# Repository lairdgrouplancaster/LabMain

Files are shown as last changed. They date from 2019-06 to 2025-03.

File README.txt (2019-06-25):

How to use this repository:
(Note: All commands are to be entered without quotation marks)

First off, you will need to install Git onto your local machine. Follow this link: "https://git-scm.com/" and download the appropriate version. If unsure whether git is installed on your local machine, open a command prompt and type: "git --version" and see whether it is installed. 

To start with, open up either the command prompt or GitBash and configure your Git username and email, which will be used to identify you as the author for each commit. This is done by entering the following: "git config --global user.name "YOUR_USERNAME"" and "git config --global user.email "YOUR_EMAIL@example.com""

Once this has been done, you can clone the repository to your local device by inputting the following command: "git clone https://github.com/lairdgrouplancaster/LabMain.git" which will then copy all of the files from the repository and place them in a folder of the same name. 

Once cloned, you can navigate to the directory in the command prompt, and then check to see your remote repositories by using: "git remote -v" This will usually show what remote repository it is (usually origin). If this isn't showing, you can manually add these repositories. 

AT THE START OF EACH SESSION: Ensure that you have an up-to-date copy of the repository by using: "git pull origin master"

To check the changes made in the local directory, you can use "git status" to check any modifications that you have made to the file itself, and use "git diff" to view the differences between the local changes to the repository versions that were previously cloned/pulled

You can add changes to the local version of the repository by using the following command: "git add FILE OR FOLDER" or "git add ." to ready either a file, folder or all files and folders for commiting. Then input: "git commit -m "COMMENT ON CHANGE AND INTENTION"" 

To push all of the local commits to the remote repository on GitHub, you can use the following command: "git push origin master", where you can replace origin for the name of a different remote repository and master for a different branch. 

All of this can also be done in the browser as well, and any additional pieces of information (Creating branches, forks etc.) can be found online, usually on the GitHub website itself.

Using a previous version of the repository:

After cloning the repository, look at the recent logs by using the command: "git log --oneline". Select the version of the roll back you want, and then make note of the first 5 characters of the unique number and use: "git checkout (5 characters)". Alternatively, you can use this function based on dates instead, for example if I wanted to revert back 10 days ago, I would input: "git checkout @{10.days.ago}"

Current Files: 

.gitignore: This file tells Git what files and folders to ignore when pulling or pushing updates. Currently only ignores the cache folder for Python.
LICENSE: This is where all licenses for software can be found, and can be added. Currently contains license for GNU
README: Current file, explains how to get started and what files are contained in this repository

Current Folders:

LiamColman: Liam's work uploaded onto Github for storage

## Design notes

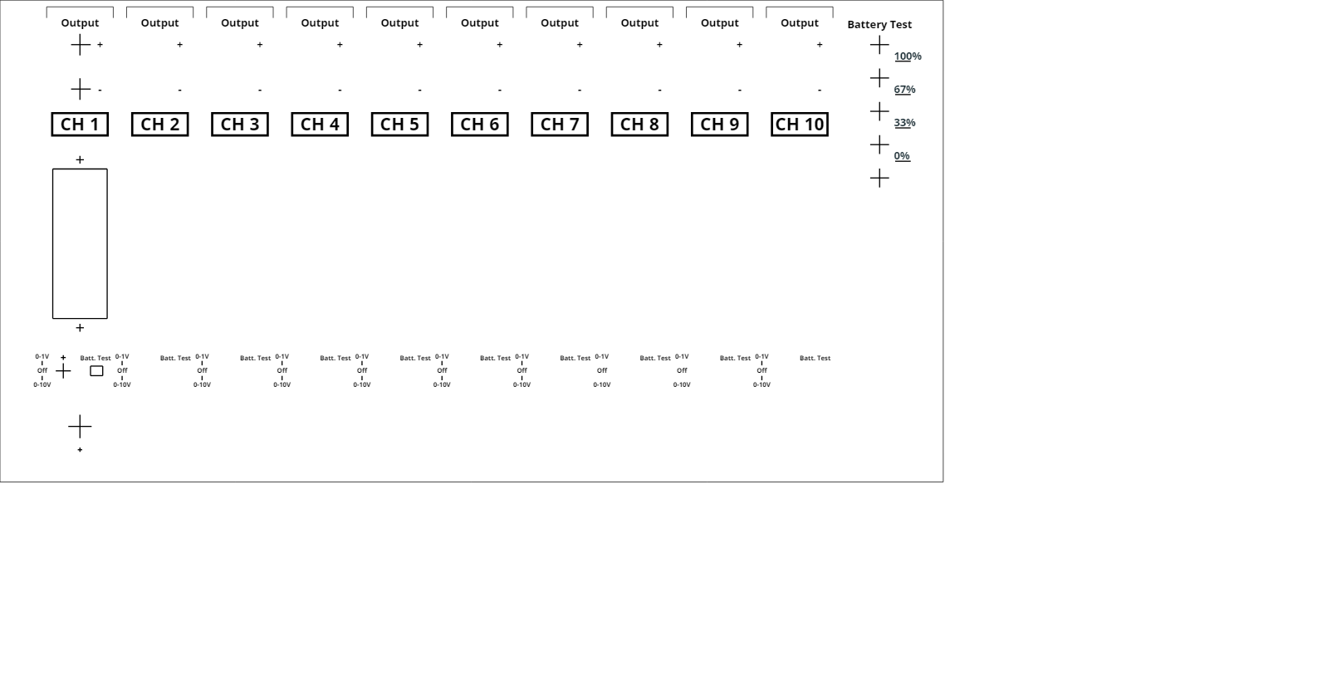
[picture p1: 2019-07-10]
LiamsWork/VoltageRegulator/FrontPanelDesign/VoltageSourceFrontPanel.png

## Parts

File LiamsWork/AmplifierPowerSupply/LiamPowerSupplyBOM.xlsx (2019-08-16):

Bill of materials for amplifier power supply
Part Name | Manufacturer | Manufacturer Part Number | PCB Reference | Qty | Description | SMD, TH or Other (BGA, QFN etc.) | Comment
1206 Capacitor | PCBTrain Free Stock | 1206-1uF-50V (MC1206B104K500CT) | C1, C3 | 2 | CAPACITOR; 1206; 50V; 10%; X7R; -55+125C | SMD | Farnell (https://uk.farnell.com/multicomp/mc1206b104k500ct/cap-mlcc-x7r-100nf-50v-1206/dp/1759361)
1206 Capacitor | AVX Corporation | TPSA106K010R0900 | C2, C4 | 2 | Tantalum capacitor; 1206; 10V; 10u | SMD |  | Digikey (https://www.digikey.co.uk/product-detail/en/avx-corporation/TPSA106K010R0900/478-1751-1-ND/564783)
Fuseholder | EATON BUSSMANN SERIES | HTC-100M | F1, F2 | 2 | Fuseholder; 5A; 250V | TH | Farnell (https://uk.farnell.com/eaton-bussmann-series/htc-100m/fuse-holder-pcb-250v-5a/dp/2550634)
2 pin headers | SULLINS CONNECTOR SOLUTIONS | GEC01DAAN | J1, J2, J3, J4 | 4 | Male header; 2 pin; 2 row; 2.54mm pitch | TH |  | Digikey (https://www.digikey.co.uk/product-detail/en/sullins-connector-solutions/GEC01DAAN/S9682-ND/4552155)
4 pin header | SULLINS CONNECTOR SOLUTIONS | PEC04SAAN | J5 | 1 | Male header; 4 pin; 1 row; 2.54mm pitch | TH |  | Digikey (https://www.digikey.com/product-detail/en/sullins-connector-solutions/PEC04SAAN/S1012E-04-ND/859157)
Low-Dropout voltage regulator | TEXAS INSTRUMENTS | TPS7250 | LD01 | 1 | 5V output; low quiescent current; power good status; PDIP package | TH | Mouser (https://www.mouser.co.uk/ProductDetail/Texas-Instruments/TPS7250QP?qs=sGAEpiMZZMsGz1a6aV8DcPXeWoVS0FnzUEk95Vl5yAE%3D) | Texas Instuments (http://www.ti.com/product/TPS72)
DIP Socket | Winslow | W30508TRC | LD01 | 1 | 8 pin; 7.62mm row spacing; 2.54mm pitch | TH |  | RS Components (https://uk.rs-online.com/web/p/dil-sockets/0813115/)
Quad transistors | CENTRAL SEMICONDUCTOR | MPQ3904 | Q1 | 1 | Quad bipolar transistors; NPN; TO-116 package | TH | Mouser (https://www.mouser.co.uk/ProductDetail/Central-Semiconductor/MPQ3904?qs=Ypxpq5eNvNUHCP5TyaTdcA%3D%3D)
DIP Socket | ARIES | 14-3518-10 | Q1 | 1 | 14 pin; 7.62mm row spacing; 2.54mm pitch | TH | Farnell (https://uk.farnell.com/aries/14-3518-10/socket-dip-14way/dp/1674785)
0805 Resistor | PCBTrain Free Stock | 0805-1K2 | R1, R6 | 2 | RESISTOR; 0805; 0.125W; 100ppm; 1%; 150V; -55+125C; 1.2k | SMD
0805 Resistor | PCBTrain Free Stock | 0805-240K | R2 | 1 | RESISTOR; 0805; 0.125W; 100ppm; 1%; 150V; -55+125C; 240k | SMD
0805 Resistor | PCBTrain Free Stock | 0805-150R | R3, R5 | 2 | RESISTOR; 0805; 0.125W; 100ppm; 1%; 150V; -55+125C; 150R | SMD
0805 Resistor | PCBTrain Free Stock | 0805-270R | R4 | 1 | RESISTOR; 0805; 0.125W; 100ppm; 1%; 150V; -55+125C; 270R | SMD
0805 Resistor | PCBTrain Free Stock | 0805-56R | R7 | 1 | RESISTOR; 0805; 0.125W; 100ppm; 1%; 150V; -55+125C; 56R | SMD
0805 Resistor | PCBTrain Free Stock | 0805-33R | R8 | 1 | RESISTOR; 0805; 0.125W; 100ppm; 1%; 150V; -55+125C: 33R | SMD
0805 Resistor | PCBTrain Free Stock | 0805-10R | R9 | 1 | RESISTOR; 0805; 0.125W; 100ppm; 1%; 150V; -55+125C; 10R | SMD
0805 Resistor | PCBTrain Free Stock | 0805-470K | R10 | 1 | RESISTOR; 0805; 0.125W; 100ppm; 1%; 150V; -55+125C; 470k | SMD
0805 Resistor | PCBTrain Free Stock | 0805-100R | R11, R12 | 2 | RESISTOR; 0805; 0.125W; 100ppm; 1%; 150V; -55+125C; 100R | SMD
Thryristor | STMicroelectronics | X0205MA 1BA2 | SCR1 | 1 | 1.25A sensitive gate SCR | TH | Mouser (https://www.mouser.co.uk/ProductDetail/STMicroelectronics/X0205MA-1BA2/?qs=rbJCU8ygG7CkfsITI88o%2Fw%3D%3D)
Zener diode | Panasonic | DZ2W04300L | Z1 | 1 | 4.3V zener diode; Mini2 package | SMD | Mouser (https://www.mouser.co.uk/ProductDetail/Panasonic/DZ2W04300L?qs=VO99igtUVKlrlP3g8MwZQg%3D%3D) | Digikey (https://www.digikey.com/product-detail/en/panasonic-electronic-components/DZ2W04300L/DZ2W04300LCT-ND/3595040)

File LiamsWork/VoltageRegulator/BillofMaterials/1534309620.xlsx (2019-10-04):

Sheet: 0201 RESISTORS
VALUE | NEL P/N | DESCRIPTION (type; size; power; TC; tolerance; volt.; temp.;)
0R0 | 0201-0R | RESISTOR; 0201; 0.05W; 400ppm; ≤50mΩ; 25V; -55+125C
1R0 | 0201-1R | RESISTOR; 0201; 0.05W; 400ppm; 1%; 25V; -55+125C;
1R1 | 0201-1R1 | RESISTOR; 0201; 0.05W; 400ppm; 1%; 25V; -55+125C;
1R2 | 0201-1R2 | RESISTOR; 0201; 0.05W; 400ppm; 1%; 25V; -55+125C;
1R5 | 0201-1R5 | RESISTOR; 0201; 0.05W; 400ppm; 1%; 25V; -55+125C;
1R8 | 0201-1R8 | RESISTOR; 0201; 0.05W; 400ppm; 1%; 25V; -55+125C;
2R0 | 0201-2R | RESISTOR; 0201; 0.05W; 400ppm; 1%; 25V; -55+125C;
2R2 | 0201-2R2 | RESISTOR; 0201; 0.05W; 400ppm; 1%; 25V; -55+125C;
2R7 | 0201-2R7 | RESISTOR; 0201; 0.05W; 400ppm; 1%; 25V; -55+125C;
3R0 | 0201-3R | RESISTOR; 0201; 0.05W; 400ppm; 1%; 25V; -55+125C;
3R3 | 0201-3R3 | RESISTOR; 0201; 0.05W; 400ppm; 1%; 25V; -55+125C;
3R9 | 0201-3R9 | RESISTOR; 0201; 0.05W; 400ppm; 1%; 25V; -55+125C;
4R7 | 0201-4R7 | RESISTOR; 0201; 0.05W; 400ppm; 1%; 25V; -55+125C;
5R1 | 0201-5R1 | RESISTOR; 0201; 0.05W; 400ppm; 1%; 25V; -55+125C;
5R6 | 0201-5R6 | RESISTOR; 0201; 0.05W; 400ppm; 1%; 25V; -55+125C;
6R8 | 0201-6R8 | RESISTOR; 0201; 0.05W; 400ppm; 1%; 25V; -55+125C;
8R2 | 0201-8R2 | RESISTOR; 0201; 0.05W; 400ppm; 1%; 25V; -55+125C;
10R | 0201-10R | RESISTOR; 0201; 0.05W; 200ppm; 1%; 25V; -55+125C;
11R | 0201-11R | RESISTOR; 0201; 0.05W; 200ppm; 1%; 25V; -55+125C;
12R | 0201-12R | RESISTOR; 0201; 0.05W; 200ppm; 1%; 25V; -55+125C;
13R | 0201-13R | RESISTOR; 0201; 0.05W; 200ppm; 1%; 25V; -55+125C;
15R | 0201-15R | RESISTOR; 0201; 0.05W; 200ppm; 1%; 25V; -55+125C;
16R | 0201-16R | RESISTOR; 0201; 0.05W; 200ppm; 1%; 25V; -55+125C;
18R | 0201-18R | RESISTOR; 0201; 0.05W; 200ppm; 1%; 25V; -55+125C;
20R | 0201-20R | RESISTOR; 0201; 0.05W; 200ppm; 1%; 25V; -55+125C;
22R | 0201-22R | RESISTOR; 0201; 0.05W; 200ppm; 1%; 25V; -55+125C;
24R | 0201-24R | RESISTOR; 0201; 0.05W; 200ppm; 1%; 25V; -55+125C;
27R | 0201-27R | RESISTOR; 0201; 0.05W; 200ppm; 1%; 25V; -55+125C;
30R | 0201-30R | RESISTOR; 0201; 0.05W; 200ppm; 1%; 25V; -55+125C;
33R | 0201-33R | RESISTOR; 0201; 0.05W; 200ppm; 1%; 25V; -55+125C;
36R | 0201-36R | RESISTOR; 0201; 0.05W; 200ppm; 1%; 25V; -55+125C;
39R | 0201-39R | RESISTOR; 0201; 0.05W; 200ppm; 1%; 25V; -55+125C;
43R | 0201-43R | RESISTOR; 0201; 0.05W; 200ppm; 1%; 25V; -55+125C;
47R | 0201-47R | RESISTOR; 0201; 0.05W; 200ppm; 1%; 25V; -55+125C;
51R | 0201-51R | RESISTOR; 0201; 0.05W; 200ppm; 1%; 25V; -55+125C;
56R | 0201-56R | RESISTOR; 0201; 0.05W; 200ppm; 1%; 25V; -55+125C;
62R | 0201-62R | RESISTOR; 0201; 0.05W; 200ppm; 1%; 25V; -55+125C;
68R | 0201-68R | RESISTOR; 0201; 0.05W; 200ppm; 1%; 25V; -55+125C;
75R | 0201-75R | RESISTOR; 0201; 0.05W; 200ppm; 1%; 25V; -55+125C;
82R | 0201-82R | RESISTOR; 0201; 0.05W; 200ppm; 1%; 25V; -55+125C;
91R | 0201-91R | RESISTOR; 0201; 0.05W; 200ppm; 1%; 25V; -55+125C;
100R | 0201-100R | RESISTOR; 0201; 0.05W; 200ppm; 1%; 25V; -55+125C;
110R | 0201-110R | RESISTOR; 0201; 0.05W; 200ppm; 1%; 25V; -55+125C;
120R | 0201-120R | RESISTOR; 0201; 0.05W; 200ppm; 1%; 25V; -55+125C;
130R | 0201-130R | RESISTOR; 0201; 0.05W; 200ppm; 1%; 25V; -55+125C;
150R | 0201-150R | RESISTOR; 0201; 0.05W; 200ppm; 1%; 25V; -55+125C;
160R | 0201-160R | RESISTOR; 0201; 0.05W; 200ppm; 1%; 25V; -55+125C;
180R | 0201-180R | RESISTOR; 0201; 0.05W; 200ppm; 1%; 25V; -55+125C;
200R | 0201-200R | RESISTOR; 0201; 0.05W; 200ppm; 1%; 25V; -55+125C;
220R | 0201-220R | RESISTOR; 0201; 0.05W; 200ppm; 1%; 25V; -55+125C;
240R | 0201-240R | RESISTOR; 0201; 0.05W; 200ppm; 1%; 25V; -55+125C;
270R | 0201-270R | RESISTOR; 0201; 0.05W; 200ppm; 1%; 25V; -55+125C;
300R | 0201-300R | RESISTOR; 0201; 0.05W; 200ppm; 1%; 25V; -55+125C;
330R | 0201-330R | RESISTOR; 0201; 0.05W; 200ppm; 1%; 25V; -55+125C;
360R | 0201-360R | RESISTOR; 0201; 0.05W; 200ppm; 1%; 25V; -55+125C;
390R | 0201-390R | RESISTOR; 0201; 0.05W; 200ppm; 1%; 25V; -55+125C;
430R | 0201-430R | RESISTOR; 0201; 0.05W; 200ppm; 1%; 25V; -55+125C;
470R | 0201-470R | RESISTOR; 0201; 0.05W; 200ppm; 1%; 25V; -55+125C;
510R | 0201-510R | RESISTOR; 0201; 0.05W; 200ppm; 1%; 25V; -55+125C;
560R | 0201-560R | RESISTOR; 0201; 0.05W; 200ppm; 1%; 25V; -55+125C;
620R | 0201-620R | RESISTOR; 0201; 0.05W; 200ppm; 1%; 25V; -55+125C;
680R | 0201-680R | RESISTOR; 0201; 0.05W; 200ppm; 1%; 25V; -55+125C;
750R | 0201-750R | RESISTOR; 0201; 0.05W; 200ppm; 1%; 25V; -55+125C;
820R | 0201-820R | RESISTOR; 0201; 0.05W; 200ppm; 1%; 25V; -55+125C;
910R | 0201-910R | RESISTOR; 0201; 0.05W; 200ppm; 1%; 25V; -55+125C;
1K0 | 0201-1K | RESISTOR; 0201; 0.05W; 200ppm; 1%; 25V; -55+125C;
1K1 | 0201-1K1 | RESISTOR; 0201; 0.05W; 200ppm; 1%; 25V; -55+125C;
1K2 | 0201-1K2 | RESISTOR; 0201; 0.05W; 200ppm; 1%; 25V; -55+125C;
1K3 | 0201-1K3 | RESISTOR; 0201; 0.05W; 200ppm; 1%; 25V; -55+125C;
1K5 | 0201-1K5 | RESISTOR; 0201; 0.05W; 200ppm; 1%; 25V; -55+125C;
1K6 | 0201-1K6 | RESISTOR; 0201; 0.05W; 200ppm; 1%; 25V; -55+125C;
1K8 | 0201-1K8 | RESISTOR; 0201; 0.05W; 200ppm; 1%; 25V; -55+125C;
2K0 | 0201-2K | RESISTOR; 0201; 0.05W; 200ppm; 1%; 25V; -55+125C;
2K2 | 0201-2K2 | RESISTOR; 0201; 0.05W; 200ppm; 1%; 25V; -55+125C;
2K4 | 0201-2K4 | RESISTOR; 0201; 0.05W; 200ppm; 1%; 25V; -55+125C;
2K7 | 0201-2K7 | RESISTOR; 0201; 0.05W; 200ppm; 1%; 25V; -55+125C;
3K0 | 0201-3K | RESISTOR; 0201; 0.05W; 200ppm; 1%; 25V; -55+125C;
3K3 | 0201-3K3 | RESISTOR; 0201; 0.05W; 200ppm; 1%; 25V; -55+125C;
3K6 | 0201-3K6 | RESISTOR; 0201; 0.05W; 200ppm; 1%; 25V; -55+125C;
3K9 | 0201-3K9 | RESISTOR; 0201; 0.05W; 200ppm; 1%; 25V; -55+125C;
4K3 | 0201-4K3 | RESISTOR; 0201; 0.05W; 200ppm; 1%; 25V; -55+125C;
4K7 | 0201-4K7 | RESISTOR; 0201; 0.05W; 200ppm; 1%; 25V; -55+125C;
5K1 | 0201-5K1 | RESISTOR; 0201; 0.05W; 200ppm; 1%; 25V; -55+125C;
5K6 | 0201-5K6 | RESISTOR; 0201; 0.05W; 200ppm; 1%; 25V; -55+125C;
6K2 | 0201-6K2 | RESISTOR; 0201; 0.05W; 200ppm; 1%; 25V; -55+125C;
6K8 | 0201-6K8 | RESISTOR; 0201; 0.05W; 200ppm; 1%; 25V; -55+125C;
7K5 | 0201-7K5 | RESISTOR; 0201; 0.05W; 200ppm; 1%; 25V; -55+125C;
8K2 | 0201-8K2 | RESISTOR; 0201; 0.05W; 200ppm; 1%; 25V; -55+125C;
9K1 | 0201-9K1 | RESISTOR; 0201; 0.05W; 200ppm; 1%; 25V; -55+125C;
10K | 0201-10K | RESISTOR; 0201; 0.05W; 200ppm; 1%; 25V; -55+125C;
11K | 0201-11K | RESISTOR; 0201; 0.05W; 200ppm; 1%; 25V; -55+125C;
12K | 0201-12K | RESISTOR; 0201; 0.05W; 200ppm; 1%; 25V; -55+125C;
13K | 0201-13K | RESISTOR; 0201; 0.05W; 200ppm; 1%; 25V; -55+125C;
15K | 0201-15K | RESISTOR; 0201; 0.05W; 200ppm; 1%; 25V; -55+125C;
16K | 0201-16K | RESISTOR; 0201; 0.05W; 200ppm; 1%; 25V; -55+125C;
18K | 0201-18K | RESISTOR; 0201; 0.05W; 200ppm; 1%; 25V; -55+125C;
20K | 0201-20K | RESISTOR; 0201; 0.05W; 200ppm; 1%; 25V; -55+125C;
22K | 0201-22K | RESISTOR; 0201; 0.05W; 200ppm; 1%; 25V; -55+125C;
24K | 0201-24K | RESISTOR; 0201; 0.05W; 200ppm; 1%; 25V; -55+125C;
27K | 0201-27K | RESISTOR; 0201; 0.05W; 200ppm; 1%; 25V; -55+125C;
30K | 0201-30K | RESISTOR; 0201; 0.05W; 200ppm; 1%; 25V; -55+125C;
33K | 0201-33K | RESISTOR; 0201; 0.05W; 200ppm; 1%; 25V; -55+125C;
36K | 0201-36K | RESISTOR; 0201; 0.05W; 200ppm; 1%; 25V; -55+125C;
39K | 0201-39K | RESISTOR; 0201; 0.05W; 200ppm; 1%; 25V; -55+125C;
43K | 0201-43K | RESISTOR; 0201; 0.05W; 200ppm; 1%; 25V; -55+125C;
47K | 0201-47K | RESISTOR; 0201; 0.05W; 200ppm; 1%; 25V; -55+125C;
51K | 0201-51K | RESISTOR; 0201; 0.05W; 200ppm; 1%; 25V; -55+125C;
56K | 0201-56K | RESISTOR; 0201; 0.05W; 200ppm; 1%; 25V; -55+125C;
62K | 0201-62K | RESISTOR; 0201; 0.05W; 200ppm; 1%; 25V; -55+125C;
68K | 0201-68K | RESISTOR; 0201; 0.05W; 200ppm; 1%; 25V; -55+125C;
75K | 0201-75K | RESISTOR; 0201; 0.05W; 200ppm; 1%; 25V; -55+125C;
82K | 0201-82K | RESISTOR; 0201; 0.05W; 200ppm; 1%; 25V; -55+125C;
91K | 0201-91K | RESISTOR; 0201; 0.05W; 200ppm; 1%; 25V; -55+125C;
100K | 0201-100K | RESISTOR; 0201; 0.05W; 200ppm; 1%; 25V; -55+125C;
110K | 0201-110K | RESISTOR; 0201; 0.05W; 200ppm; 1%; 25V; -55+125C;
120K | 0201-120K | RESISTOR; 0201; 0.05W; 200ppm; 1%; 25V; -55+125C;
150K | 0201-150K | RESISTOR; 0201; 0.05W; 200ppm; 1%; 25V; -55+125C;
160K | 0201-160K | RESISTOR; 0201; 0.05W; 200ppm; 1%; 25V; -55+125C;
180K | 0201-180K | RESISTOR; 0201; 0.05W; 200ppm; 1%; 25V; -55+125C;
200K | 0201-200K | RESISTOR; 0201; 0.05W; 200ppm; 1%; 25V; -55+125C;
220K | 0201-220K | RESISTOR; 0201; 0.05W; 200ppm; 1%; 25V; -55+125C;
240K | 0201-240K | RESISTOR; 0201; 0.05W; 200ppm; 1%; 25V; -55+125C;
270K | 0201-270K | RESISTOR; 0201; 0.05W; 200ppm; 1%; 25V; -55+125C;
300K | 0201-300K | RESISTOR; 0201; 0.05W; 200ppm; 1%; 25V; -55+125C;
330K | 0201-330K | RESISTOR; 0201; 0.05W; 200ppm; 1%; 25V; -55+125C;
360K | 0201-360K | RESISTOR; 0201; 0.05W; 200ppm; 1%; 25V; -55+125C;
390K | 0201-390K | RESISTOR; 0201; 0.05W; 200ppm; 1%; 25V; -55+125C;
430K | 0201-430K | RESISTOR; 0201; 0.05W; 200ppm; 1%; 25V; -55+125C;
470K | 0201-470K | RESISTOR; 0201; 0.05W; 200ppm; 1%; 25V; -55+125C;
510K | 0201-510K | RESISTOR; 0201; 0.05W; 200ppm; 1%; 25V; -55+125C;
560K | 0201-560K | RESISTOR; 0201; 0.05W; 200ppm; 1%; 25V; -55+125C;
620K | 0201-620K | RESISTOR; 0201; 0.05W; 200ppm; 1%; 25V; -55+125C;
680K | 0201-680K | RESISTOR; 0201; 0.05W; 200ppm; 1%; 25V; -55+125C;
750K | 0201-750K | RESISTOR; 0201; 0.05W; 200ppm; 1%; 25V; -55+125C;
820K | 0201-820K | RESISTOR; 0201; 0.05W; 200ppm; 1%; 25V; -55+125C;
910K | 0201-910K | RESISTOR; 0201; 0.05W; 200ppm; 1%; 25V; -55+125C;
1M0 | 0201-1M | RESISTOR; 0201; 0.05W; 200ppm; 1%; 25V; -55+125C;
1M2 | 0201-1M2 | RESISTOR; 0201; 0.05W; 200ppm; 1%; 25V; -55+125C;
1M3 | 0201-1M3 | RESISTOR; 0201; 0.05W; 200ppm; 1%; 25V; -55+125C;
1M5 | 0201-1M5 | RESISTOR; 0201; 0.05W; 200ppm; 1%; 25V; -55+125C;
1M6 | 0201-1M6 | RESISTOR; 0201; 0.05W; 200ppm; 1%; 25V; -55+125C;
1M8 | 0201-1M8 | RESISTOR; 0201; 0.05W; 200ppm; 1%; 25V; -55+125C;
2M0 | 0201-2M | RESISTOR; 0201; 0.05W; 200ppm; 1%; 25V; -55+125C;
2M2 | 0201-2M2 | RESISTOR; 0201; 0.05W; 200ppm; 1%; 25V; -55+125C;
2M7 | 0201-2M7 | RESISTOR; 0201; 0.05W; 200ppm; 1%; 25V; -55+125C;
3M0 | 0201-3M | RESISTOR; 0201; 0.05W; 200ppm; 1%; 25V; -55+125C;
3M3 | 0201-3M3 | RESISTOR; 0201; 0.05W; 200ppm; 1%; 25V; -55+125C;
3M6 | 0201-3M6 | RESISTOR; 0201; 0.05W; 200ppm; 1%; 25V; -55+125C;
3M9 | 0201-3M9 | RESISTOR; 0201; 0.05W; 200ppm; 1%; 25V; -55+125C;
4M7 | 0201-4M7 | RESISTOR; 0201; 0.05W; 200ppm; 1%; 25V; -55+125C;
5M1 | 0201-5M1 | RESISTOR; 0201; 0.05W; 200ppm; 1%; 25V; -55+125C;
6M8 | 0201-6M8 | RESISTOR; 0201; 0.05W; 200ppm; 1%; 25V; -55+125C;
8M2 | 0201-8M2 | RESISTOR; 0201; 0.05W; 200ppm; 1%; 25V; -55+125C;
10M | 0201-10M | RESISTOR; 0201; 0.05W; 200ppm; 1%; 25V; -55+125C;

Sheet: 0402 RESISTORS
VALUE | NEL P/N | DESCRIPTION (type; size; power; TC; tolerance; volt.; temp.;)
0R0 | 0402-0R | RESISTOR; 0402; 0.0625W; 400ppm; ≤50mΩ; 50V; -55+125C
1R0 | 0402-1R | RESISTOR; 0402; 0.0625W; 400ppm; 1%; 50V; -55+125C
1R1 | 0402-1R1 | RESISTOR; 0402; 0.0625W; 400ppm; 1%; 50V; -55+125C
1R2 | 0402-1R2 | RESISTOR; 0402; 0.0625W; 400ppm; 1%; 50V; -55+125C
1R3 | 0402-1R3 | RESISTOR; 0402; 0.0625W; 400ppm; 1%; 50V; -55+125C
1R5 | 0402-1R5 | RESISTOR; 0402; 0.0625W; 400ppm; 1%; 50V; -55+125C
1R6 | 0402-1R6 | RESISTOR; 0402; 0.0625W; 400ppm; 1%; 50V; -55+125C
1R8 | 0402-1R8 | RESISTOR; 0402; 0.0625W; 400ppm; 1%; 50V; -55+125C
2R0 | 0402-2R | RESISTOR; 0402; 0.0625W; 400ppm; 1%; 50V; -55+125C
2R2 | 0402-2R2 | RESISTOR; 0402; 0.0625W; 400ppm; 1%; 50V; -55+125C
2R4 | 0402-2R4 | RESISTOR; 0402; 0.0625W; 400ppm; 1%; 50V; -55+125C
2R7 | 0402-2R7 | RESISTOR; 0402; 0.0625W; 400ppm; 1%; 50V; -55+125C
3R0 | 0402-3R | RESISTOR; 0402; 0.0625W; 400ppm; 1%; 50V; -55+125C
3R3 | 0402-3R3 | RESISTOR; 0402; 0.0625W; 400ppm; 1%; 50V; -55+125C
3R6 | 0402-3R6 | RESISTOR; 0402; 0.0625W; 400ppm; 1%; 50V; -55+125C
3R9 | 0402-3R9 | RESISTOR; 0402; 0.0625W; 400ppm; 1%; 50V; -55+125C
4R3 | 0402-4R3 | RESISTOR; 0402; 0.0625W; 400ppm; 1%; 50V; -55+125C
4R7 | 0402-4R7 | RESISTOR; 0402; 0.0625W; 400ppm; 1%; 50V; -55+125C
5R1 | 0402-5R1 | RESISTOR; 0402; 0.0625W; 400ppm; 1%; 50V; -55+125C
5R6 | 0402-5R6 | RESISTOR; 0402; 0.0625W; 400ppm; 1%; 50V; -55+125C
6R2 | 0402-6R2 | RESISTOR; 0402; 0.0625W; 400ppm; 1%; 50V; -55+125C
6R8 | 0402-6R8 | RESISTOR; 0402; 0.0625W; 400ppm; 1%; 50V; -55+125C
7R5 | 0402-7R5 | RESISTOR; 0402; 0.0625W; 400ppm; 1%; 50V; -55+125C
8R2 | 0402-8R2 | RESISTOR; 0402; 0.0625W; 400ppm; 1%; 50V; -55+125C
9R1 | 0402-9R1 | RESISTOR; 0402; 0.0625W; 400ppm; 1%; 50V; -55+125C
10R | 0402-10R | RESISTOR; 0402; 0.0625W; 200ppm; 1%; 50V; -55+125C
11R | 0402-11R | RESISTOR; 0402; 0.0625W; 200ppm; 1%; 50V; -55+125C
12R | 0402-12R | RESISTOR; 0402; 0.0625W; 200ppm; 1%; 50V; -55+125C
13R | 0402-13R | RESISTOR; 0402; 0.0625W; 200ppm; 1%; 50V; -55+125C
15R | 0402-15R | RESISTOR; 0402; 0.0625W; 200ppm; 1%; 50V; -55+125C
16R | 0402-16R | RESISTOR; 0402; 0.0625W; 200ppm; 1%; 50V; -55+125C
18R | 0402-18R | RESISTOR; 0402; 0.0625W; 200ppm; 1%; 50V; -55+125C
20R | 0402-20R | RESISTOR; 0402; 0.0625W; 200ppm; 1%; 50V; -55+125C
22R | 0402-22R | RESISTOR; 0402; 0.0625W; 200ppm; 1%; 50V; -55+125C
24R | 0402-24R | RESISTOR; 0402; 0.0625W; 200ppm; 1%; 50V; -55+125C
27R | 0402-27R | RESISTOR; 0402; 0.0625W; 200ppm; 1%; 50V; -55+125C
30R | 0402-30R | RESISTOR; 0402; 0.0625W; 200ppm; 1%; 50V; -55+125C
33R | 0402-33R | RESISTOR; 0402; 0.0625W; 200ppm; 1%; 50V; -55+125C
36R | 0402-36R | RESISTOR; 0402; 0.0625W; 200ppm; 1%; 50V; -55+125C
39R | 0402-39R | RESISTOR; 0402; 0.0625W; 200ppm; 1%; 50V; -55+125C
43R | 0402-43R | RESISTOR; 0402; 0.0625W; 200ppm; 1%; 50V; -55+125C
47R | 0402-47R | RESISTOR; 0402; 0.0625W; 200ppm; 1%; 50V; -55+125C
51R | 0402-51R | RESISTOR; 0402; 0.0625W; 200ppm; 1%; 50V; -55+125C
56R | 0402-56R | RESISTOR; 0402; 0.0625W; 200ppm; 1%; 50V; -55+125C
62R | 0402-62R | RESISTOR; 0402; 0.0625W; 200ppm; 1%; 50V; -55+125C
68R | 0402-68R | RESISTOR; 0402; 0.0625W; 200ppm; 1%; 50V; -55+125C
75R | 0402-75R | RESISTOR; 0402; 0.0625W; 200ppm; 1%; 50V; -55+125C
82R | 0402-82R | RESISTOR; 0402; 0.0625W; 200ppm; 1%; 50V; -55+125C
91R | 0402-91R | RESISTOR; 0402; 0.0625W; 200ppm; 1%; 50V; -55+125C
100R | 0402-100R | RESISTOR; 0402; 0.0625W; 100ppm; 1%; 50V; -55+125C
110R | 0402-110R | RESISTOR; 0402; 0.0625W; 100ppm; 1%; 50V; -55+125C
120R | 0402-120R | RESISTOR; 0402; 0.0625W; 100ppm; 1%; 50V; -55+125C
130R | 0402-130R | RESISTOR; 0402; 0.0625W; 100ppm; 1%; 50V; -55+125C
150R | 0402-150R | RESISTOR; 0402; 0.0625W; 100ppm; 1%; 50V; -55+125C
160R | 0402-160R | RESISTOR; 0402; 0.0625W; 100ppm; 1%; 50V; -55+125C
180R | 0402-180R | RESISTOR; 0402; 0.0625W; 100ppm; 1%; 50V; -55+125C
200R | 0402-200R | RESISTOR; 0402; 0.0625W; 100ppm; 1%; 50V; -55+125C
220R | 0402-220R | RESISTOR; 0402; 0.0625W; 100ppm; 1%; 50V; -55+125C
240R | 0402-240R | RESISTOR; 0402; 0.0625W; 100ppm; 1%; 50V; -55+125C
270R | 0402-270R | RESISTOR; 0402; 0.0625W; 100ppm; 1%; 50V; -55+125C
300R | 0402-300R | RESISTOR; 0402; 0.0625W; 100ppm; 1%; 50V; -55+125C
330R | 0402-330R | RESISTOR; 0402; 0.0625W; 100ppm; 1%; 50V; -55+125C
360R | 0402-360R | RESISTOR; 0402; 0.0625W; 100ppm; 1%; 50V; -55+125C
390R | 0402-390R | RESISTOR; 0402; 0.0625W; 100ppm; 1%; 50V; -55+125C
430R | 0402-430R | RESISTOR; 0402; 0.0625W; 100ppm; 1%; 50V; -55+125C
470R | 0402-470R | RESISTOR; 0402; 0.0625W; 100ppm; 1%; 50V; -55+125C
510R | 0402-510R | RESISTOR; 0402; 0.0625W; 100ppm; 1%; 50V; -55+125C
560R | 0402-560R | RESISTOR; 0402; 0.0625W; 100ppm; 1%; 50V; -55+125C
620R | 0402-620R | RESISTOR; 0402; 0.0625W; 100ppm; 1%; 50V; -55+125C
680R | 0402-680R | RESISTOR; 0402; 0.0625W; 100ppm; 1%; 50V; -55+125C
750R | 0402-750R | RESISTOR; 0402; 0.0625W; 100ppm; 1%; 50V; -55+125C
820R | 0402-820R | RESISTOR; 0402; 0.0625W; 100ppm; 1%; 50V; -55+125C
910R | 0402-910R | RESISTOR; 0402; 0.0625W; 100ppm; 1%; 50V; -55+125C
1K0 | 0402-1K | RESISTOR; 0402; 0.0625W; 100ppm; 1%; 50V; -55+125C
1K1 | 0402-1K1 | RESISTOR; 0402; 0.0625W; 100ppm; 1%; 50V; -55+125C
1K2 | 0402-1K2 | RESISTOR; 0402; 0.0625W; 100ppm; 1%; 50V; -55+125C
1K3 | 0402-1K3 | RESISTOR; 0402; 0.0625W; 100ppm; 1%; 50V; -55+125C
1K5 | 0402-1K5 | RESISTOR; 0402; 0.0625W; 100ppm; 1%; 50V; -55+125C
1K6 | 0402-1K6 | RESISTOR; 0402; 0.0625W; 100ppm; 1%; 50V; -55+125C
1K8 | 0402-1K8 | RESISTOR; 0402; 0.0625W; 100ppm; 1%; 50V; -55+125C
2K0 | 0402-2K | RESISTOR; 0402; 0.0625W; 100ppm; 1%; 50V; -55+125C
2K2 | 0402-2K2 | RESISTOR; 0402; 0.0625W; 100ppm; 1%; 50V; -55+125C
2K4 | 0402-2K4 | RESISTOR; 0402; 0.0625W; 100ppm; 1%; 50V; -55+125C
2K7 | 0402-2K7 | RESISTOR; 0402; 0.0625W; 100ppm; 1%; 50V; -55+125C
3K0 | 0402-3K | RESISTOR; 0402; 0.0625W; 100ppm; 1%; 50V; -55+125C
3K3 | 0402-3K3 | RESISTOR; 0402; 0.0625W; 100ppm; 1%; 50V; -55+125C
3K6 | 0402-3K6 | RESISTOR; 0402; 0.0625W; 100ppm; 1%; 50V; -55+125C
3K9 | 0402-3K9 | RESISTOR; 0402; 0.0625W; 100ppm; 1%; 50V; -55+125C
4K3 | 0402-4K3 | RESISTOR; 0402; 0.0625W; 100ppm; 1%; 50V; -55+125C
4K7 | 0402-4K7 | RESISTOR; 0402; 0.0625W; 100ppm; 1%; 50V; -55+125C
5K1 | 0402-5K1 | RESISTOR; 0402; 0.0625W; 100ppm; 1%; 50V; -55+125C
5K6 | 0402-5K6 | RESISTOR; 0402; 0.0625W; 100ppm; 1%; 50V; -55+125C
6K2 | 0402-6K2 | RESISTOR; 0402; 0.0625W; 100ppm; 1%; 50V; -55+125C
6K8 | 0402-6K8 | RESISTOR; 0402; 0.0625W; 100ppm; 1%; 50V; -55+125C
7K5 | 0402-7K5 | RESISTOR; 0402; 0.0625W; 100ppm; 1%; 50V; -55+125C
8K2 | 0402-8K2 | RESISTOR; 0402; 0.0625W; 100ppm; 1%; 50V; -55+125C
9K1 | 0402-9K1 | RESISTOR; 0402; 0.0625W; 100ppm; 1%; 50V; -55+125C
10K | 0402-10K | RESISTOR; 0402; 0.0625W; 100ppm; 1%; 50V; -55+125C
11K | 0402-11K | RESISTOR; 0402; 0.0625W; 100ppm; 1%; 50V; -55+125C
12K | 0402-12K | RESISTOR; 0402; 0.0625W; 100ppm; 1%; 50V; -55+125C
13K | 0402-13K | RESISTOR; 0402; 0.0625W; 100ppm; 1%; 50V; -55+125C
15K | 0402-15K | RESISTOR; 0402; 0.0625W; 100ppm; 1%; 50V; -55+125C
16K | 0402-16K | RESISTOR; 0402; 0.0625W; 100ppm; 1%; 50V; -55+125C
18K | 0402-18K | RESISTOR; 0402; 0.0625W; 100ppm; 1%; 50V; -55+125C
20K | 0402-20K | RESISTOR; 0402; 0.0625W; 100ppm; 1%; 50V; -55+125C
22K | 0402-22K | RESISTOR; 0402; 0.0625W; 100ppm; 1%; 50V; -55+125C
24K | 0402-24K | RESISTOR; 0402; 0.0625W; 100ppm; 1%; 50V; -55+125C
27K | 0402-27K | RESISTOR; 0402; 0.0625W; 100ppm; 1%; 50V; -55+125C
30K | 0402-30K | RESISTOR; 0402; 0.0625W; 100ppm; 1%; 50V; -55+125C
33K | 0402-33K | RESISTOR; 0402; 0.0625W; 100ppm; 1%; 50V; -55+125C
36K | 0402-36K | RESISTOR; 0402; 0.0625W; 100ppm; 1%; 50V; -55+125C
39K | 0402-39K | RESISTOR; 0402; 0.0625W; 100ppm; 1%; 50V; -55+125C
43K | 0402-43K | RESISTOR; 0402; 0.0625W; 100ppm; 1%; 50V; -55+125C
47K | 0402-47K | RESISTOR; 0402; 0.0625W; 100ppm; 1%; 50V; -55+125C
51K | 0402-51K | RESISTOR; 0402; 0.0625W; 100ppm; 1%; 50V; -55+125C
56K | 0402-56K | RESISTOR; 0402; 0.0625W; 100ppm; 1%; 50V; -55+125C
62K | 0402-62K | RESISTOR; 0402; 0.0625W; 100ppm; 1%; 50V; -55+125C
68K | 0402-68K | RESISTOR; 0402; 0.0625W; 100ppm; 1%; 50V; -55+125C
75K | 0402-75K | RESISTOR; 0402; 0.0625W; 100ppm; 1%; 50V; -55+125C
82K | 0402-82K | RESISTOR; 0402; 0.0625W; 100ppm; 1%; 50V; -55+125C
91K | 0402-91K | RESISTOR; 0402; 0.0625W; 100ppm; 1%; 50V; -55+125C
100K | 0402-100K | RESISTOR; 0402; 0.0625W; 100ppm; 1%; 50V; -55+125C
110K | 0402-110K | RESISTOR; 0402; 0.0625W; 100ppm; 1%; 50V; -55+125C
120K | 0402-120K | RESISTOR; 0402; 0.0625W; 100ppm; 1%; 50V; -55+125C
130K | 0402-130K | RESISTOR; 0402; 0.0625W; 100ppm; 1%; 50V; -55+125C
150K | 0402-150K | RESISTOR; 0402; 0.0625W; 100ppm; 1%; 50V; -55+125C
160K | 0402-160K | RESISTOR; 0402; 0.0625W; 100ppm; 1%; 50V; -55+125C
180K | 0402-180K | RESISTOR; 0402; 0.0625W; 100ppm; 1%; 50V; -55+125C
200K | 0402-200K | RESISTOR; 0402; 0.0625W; 100ppm; 1%; 50V; -55+125C
220K | 0402-220K | RESISTOR; 0402; 0.0625W; 100ppm; 1%; 50V; -55+125C
240K | 0402-240K | RESISTOR; 0402; 0.0625W; 100ppm; 1%; 50V; -55+125C
270K | 0402-270K | RESISTOR; 0402; 0.0625W; 100ppm; 1%; 50V; -55+125C
300K | 0402-300K | RESISTOR; 0402; 0.0625W; 100ppm; 1%; 50V; -55+125C
330K | 0402-330K | RESISTOR; 0402; 0.0625W; 100ppm; 1%; 50V; -55+125C
360K | 0402-360K | RESISTOR; 0402; 0.0625W; 100ppm; 1%; 50V; -55+125C
390K | 0402-390K | RESISTOR; 0402; 0.0625W; 100ppm; 1%; 50V; -55+125C
430K | 0402-430K | RESISTOR; 0402; 0.0625W; 100ppm; 1%; 50V; -55+125C
470K | 0402-470K | RESISTOR; 0402; 0.0625W; 100ppm; 1%; 50V; -55+125C
510K | 0402-510K | RESISTOR; 0402; 0.0625W; 100ppm; 1%; 50V; -55+125C
560K | 0402-560K | RESISTOR; 0402; 0.0625W; 100ppm; 1%; 50V; -55+125C
620K | 0402-620K | RESISTOR; 0402; 0.0625W; 100ppm; 1%; 50V; -55+125C
680K | 0402-680K | RESISTOR; 0402; 0.0625W; 100ppm; 1%; 50V; -55+125C
750K | 0402-750K | RESISTOR; 0402; 0.0625W; 100ppm; 1%; 50V; -55+125C
820K | 0402-820K | RESISTOR; 0402; 0.0625W; 100ppm; 1%; 50V; -55+125C
910K | 0402-910K | RESISTOR; 0402; 0.0625W; 100ppm; 1%; 50V; -55+125C
1M0 | 0402-1M | RESISTOR; 0402; 0.0625W; 100ppm; 1%; 50V; -55+125C
1M1 | 0402-1M1 | RESISTOR; 0402; 0.0625W; 100ppm; 1%; 50V; -55+125C
1M2 | 0402-1M2 | RESISTOR; 0402; 0.0625W; 100ppm; 1%; 50V; -55+125C
1M3 | 0402-1M3 | RESISTOR; 0402; 0.0625W; 100ppm; 1%; 50V; -55+125C
1M5 | 0402-1M5 | RESISTOR; 0402; 0.0625W; 100ppm; 1%; 50V; -55+125C
1M6 | 0402-1M6 | RESISTOR; 0402; 0.0625W; 100ppm; 1%; 50V; -55+125C
1M8 | 0402-1M8 | RESISTOR; 0402; 0.0625W; 100ppm; 1%; 50V; -55+125C
2M0 | 0402-2M | RESISTOR; 0402; 0.0625W; 100ppm; 1%; 50V; -55+125C
2M2 | 0402-2M2 | RESISTOR; 0402; 0.0625W; 100ppm; 1%; 50V; -55+125C
2M4 | 0402-2M4 | RESISTOR; 0402; 0.0625W; 100ppm; 1%; 50V; -55+125C
2M7 | 0402-2M7 | RESISTOR; 0402; 0.0625W; 100ppm; 1%; 50V; -55+125C
3M0 | 0403-3M | RESISTOR; 0402; 0.0625W; 100ppm; 1%; 50V; -55+125C
3M3 | 0402-3M3 | RESISTOR; 0402; 0.0625W; 100ppm; 1%; 50V; -55+125C
3M6 | 0402-3M6 | RESISTOR; 0402; 0.0625W; 100ppm; 1%; 50V; -55+125C
3M9 | 0402-3M9 | RESISTOR; 0402; 0.0625W; 100ppm; 1%; 50V; -55+125C
4M3 | 0402-4M3 | RESISTOR; 0402; 0.0625W; 100ppm; 1%; 50V; -55+125C
4M7 | 0402-4M7 | RESISTOR; 0402; 0.0625W; 100ppm; 1%; 50V; -55+125C
5M1 | 0402-5M1 | RESISTOR; 0402; 0.0625W; 100ppm; 1%; 50V; -55+125C
5M6 | 0402-5M6 | RESISTOR; 0402; 0.0625W; 100ppm; 1%; 50V; -55+125C
6M2 | 0402-6M2 | RESISTOR; 0402; 0.0625W; 100ppm; 1%; 50V; -55+125C
6M8 | 0402-6M8 | RESISTOR; 0402; 0.0625W; 100ppm; 1%; 50V; -55+125C
7M5 | 0402-7M5 | RESISTOR; 0402; 0.0625W; 100ppm; 1%; 50V; -55+125C
8M2 | 0402-8M2 | RESISTOR; 0402; 0.0625W; 100ppm; 1%; 50V; -55+125C
9M1 | 0402-9M1 | RESISTOR; 0402; 0.0625W; 100ppm; 1%; 50V; -55+125C
10M | 0402-10M | RESISTOR; 0402; 0.0625W; 100ppm; 1%; 50V; -55+125C
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

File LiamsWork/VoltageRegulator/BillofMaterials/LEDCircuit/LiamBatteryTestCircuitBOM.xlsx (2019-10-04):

Bill of materials for Battery testing PCB (ONE BOARD)
Part Name | Manufacturer | Manufacturer Part Number | PCB Reference | Qty | Description | SMD, TH or Other (BGA, QFN etc.) | Link
Quad Comparator | ON Semiconductor/Texas Instruments | LM339AM | U1 | 1 | 14-SOP Package, 4 independent voltage comparators, 1.3µs response time | SMD | Farnell (https://uk.farnell.com/texas-instruments/lm339am/comparator-quad-smd-soic14-339/dp/9490485?st=LM339AM) | Digikey (https://www.digikey.co.uk/product-detail/en/on-semiconductor/LM339AM/LM339AMFS-ND/1051433)
Zener Diode | Nexperia | BZX84-C10,215 | D1 | 1 | SOT23 Package, 10V, 250mW power dissipation, 5% | SMD | Farnell (https://uk.farnell.com/nexperia/bzx84-c10-215/diode-zener-10v-250mw-to-236ab/dp/2319201) | RS Components (https://uk.rs-online.com/web/p/zener-diodes/1512797/)
Trimpot | Bourns | 3266W-1-123LF | VR1 | 1 | 12k trimmable resistance, 10% | TH | Farnell (https://uk.farnell.com/bourns/3266w-1-123lf/trimmer-pot-12kohm-10-12turn-th/dp/2328453?ost=3266W-1-123LF&ddkey=https%3Aen-GB%2FEl) | Digikey (https://www.digikey.com/product-detail/en/bourns-inc/3266W-1-123LF/3266W-1-123LF-ND/2535441)
LED | MULTICOMP | MC19040001 | LED1, LED2 | 2 | Green | N/A | Farnell (https://uk.farnell.com/multicomp/mc19040001/led-indicator-5mm-green/dp/1105246)
LED | MULTICOMP | MC19040002 | LED4 | 1 | Yellow | N/A | Farnell (https://uk.farnell.com/multicomp/mc19040002/led-indicator-5mm-yellow/dp/1105247?ost=MC19040002)
LED | MULTICOMP | MC19040008 | LED3 | 1 | Orange | N/A | Farnell (https://uk.farnell.com/multicomp/mc19040008/led-indicator-5mm-orange/dp/1105248?ost=MC19040008&ddkey=https%3Aen-GB%2FElement1)
LED | MULTICOMP | MC19040003 | LED5 | 1 | Red | N/A | Farnell (https://uk.farnell.com/multicomp/mc19040003/led-indicator-5mm-he-red/dp/1105245?ost=MC19040003)
Resistor | Panasonic | ERA6AEB102V | R13 - R17 | 5 | 1k, Thin film, 25ppm, 0.1% | SMD | Farnell (https://uk.farnell.com/panasonic/era6aeb102v/res-1k-0-1-0-125w-0805-thin-film/dp/1577659)
Resistor | TT ELECTRONICS/ WELWYN | PCF0805-13-620R-B-T1. | R1 | 1 | 620R, Thin film, 5ppm, 0.1% | SMD | Farnell (https://uk.farnell.com/tt-electronics-welwyn/pcf0805-13-620r-b-t1/res-620r-0-1-0-1w-0805-thin-film/dp/1108858)
Resistor | Pansonic | ERA6AEB332V | R2 | 1 | 3.3k, Thin film, 25ppm, 0.1% | SMD | Farnell (https://uk.farnell.com/panasonic/era6aeb332v/res-3k3-0-1-0-125w-0805-thin-film/dp/1577665)
Resistor | TE CONNECTIVITY | CPF-A-0805B82KE1 | R4 | 1 | 82k, Thin film, 25ppm, 0.1% | SMD | Farnell (Low stock) (https://uk.farnell.com/te-connectivity/cpf-a-0805b82ke1/res-82k-0-1-0805-thin-film/dp/2484016RL)
Resistor | Panasonic | ERA6AEB473V | R5, R7, R8, R9, R11 | 5 | 47k, Thin film, 25ppm, 0.1% | SMD | Farnell (https://uk.farnell.com/panasonic/era6aeb473v/res-47k-0-1-0-125w-0805-thin-film/dp/1577681)
Resistor | Panasonic | ERA6AEB333V | R6 | 1 | 33k, Thin film, 10ppm, 0.05% | SMD | Farnell (https://uk.farnell.com/panasonic/era6aeb333v/res-33k-0-1-0-125w-0805-thin-film/dp/1577679?st=RESISTOR%20THIN%20FILM)
Resistor | Panasonic | ERA6AEB103V | R3 | 1 | 10k, Thin film, 25ppm, 0.1% | SMD | Farnell (https://uk.farnell.com/panasonic/era6aeb103v/res-10k-0-1-0-125w-0805-thin-film/dp/1577673?st=RESISTOR%20THIN%20FILM)
Resistor | TE CONNECTIVITY | RN73C2A57K6BTDF | R10 | 1 | 57.6k, Thin film, 25ppm, 0.1% | SMD | Farnell (https://uk.farnell.com/te-connectivity/rn73c2a57k6btdf/res-57k6-0-1-0-1w-0805-thin-film/dp/1140994)
Resistor | Panasonic | ERA6AEB683V | R12 | 1 | 68k, Thin film, 25ppm, 0.1% | SMD | Farnell (https://uk.farnell.com/panasonic/era6aeb683v/res-68k-0-1-0-125w-0805-thin-film/dp/1577684)
Screw Terminal | CAMDENBOSS | CTB5000/2 | BATTERYBUS, LED1, LED2, LED3, LED4, LED5 | 6 | 2 Pole, Screw-in | TH | Farnell (https://uk.farnell.com/camdenboss/ctb5000-2/terminal-block-wire-to-brd-2pos/dp/151789)

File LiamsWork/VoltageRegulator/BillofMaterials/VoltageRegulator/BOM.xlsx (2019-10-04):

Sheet: VoltageSourceBOM
Bill of materials for Voltage Source
Part Name | Manufacturer | Manufacturer Part Number | PCB Reference | Qty | Description | SMD or TH | Link | Comment
Capacitor | EPCOS | B32529C1103J189 | C1 | 1 | 10nF, DC Film, 100V | TH | Here (https://uk.farnell.com/epcos/b32529c1103j189/cap-0-01-f-100v-5-pet/dp/2315548?st=B32529C1103J189)
Capacitor | Panasonic | ECW-FD2E475J | C2 | 1 | 4.7µF, DC Film, 450V | TH | Here (https://uk.farnell.com/panasonic/ecwfd2w475j/cap-4-7-f-450v-5-pp/dp/2805916?ost=ECW_FD2W475j&ddkey=https%3Aen-GB%2FElement14_Unit)
Capacitor | Panasonic | ECW-FD2E105J | C3 | 1 | 1µF, DC Film, 450V | TH | There (https://uk.farnell.com/panasonic/ecwfd2w105j/cap-1-f-450v-5-pp/dp/2805908?st=ECW_FD2W105J)
Screw Terminal | CAMDENBOSS | CTB500/2 | LED, Batt, DPDT-On-Off, Out | 4 | 2 pole, Screw | TH | Where (https://uk.farnell.com/camdenboss/ctb5000-2/terminal-block-wire-to-brd-2pos/dp/151789)
Screw Terminal | CAMDENBOSS | CTB500/3 | Potentiometer, DPDT-Voltage-Range | 2 | 3 pole, Screw | TH | Hare (https://uk.farnell.com/camdenboss/ctb5000-3/terminal-block-wire-to-brd-3pos/dp/151790?MER=bn_level5_5NP_EngagementRecSingleItem_1)
Op Amp | LINEAR TECHNOLOGY | LT1494IN8 | U1 | 1 | 1.5µA, 36V supply, Low noise | TH | Lair (https://www.digikey.co.uk/product-detail/en/linear-technology-analog-devices/LT1494IN8-PBF/LT1494IN8-PBF-ND/889001)
Resistor | Panasonic | ERA6AEB474V | R1 | 1 | 470k, 0.1%, 0.125W, 0805, Thin film | SMD | Chair (https://uk.farnell.com/panasonic/era6aeb474v/res-470k-0-1-0-125w-0805-thin/dp/1577695?st=ERA6AEB474v)
Resistor | Panasonic | ERA6AEB221V | R2 | 1 | 220R, 0.1%, 0.125W, 0805, Thin film | SMD | Tear (https://uk.farnell.com/panasonic/era6aeb221v/res-220r-0-1-0-125w-0805-thin/dp/1577649?st=ERA6AEB221v)
Resistor | Panasonic | ERA6AEB824V | R7 | 1 | 820k, 0.1%, 0.125W, 0805, Thin film | SMD | Bare (https://uk.farnell.com/panasonic/era6aeb824v/res-820k-0-1-0-125w-0805-thin/dp/1577698?st=ERA6AEB824v)
Resistor | Panasonic | ERA6AEB4993V | R9 | 1 | 499k, 0.1%, 0.125W, 0805, Thin film | SMD | Pear (https://uk.farnell.com/panasonic/era6aeb4993v/res-499k-0-1-0-125w-0805-thin/dp/1810772?st=ERA6AEB4993v)
Resistor | TE CONNECTIVITY | CPF-A-0805B1M0E1 | R4 | 1 | 1M, 0.1%, 0.1W, 0805, Thin film | SMD | Bear (https://uk.farnell.com/te-connectivity/cpf-a-0805b1m0e1/res-1m-0-1-0805-thin-film/dp/2483968?st=pansonic%20resistor%20080%201Mohm)
Resistor | Panasonic | Can't Find Thin Film | R5 | 1 | 6.81M | SMD
Resistor | VISHAY | PNM0805E5001BST5 | R3, R6 | 2 | 5k, 0.1%, 0.2W, 0805, Thin Film | SMD | Eclair (https://www.mouser.co.uk/ProductDetail/Vishay-Thin-Film/PNM0805E5001BST5)
Trimmer | BOURNS | TC33X-2-104E | VR1 | 1 | 100k trim, 100mW, 1 turn | SMD | Wear (https://uk.farnell.com/bourns/tc33x-2-104e/trimmer-100k-3mm/dp/1689864?st=TC33X-2-104E)
Trimmer | BOURNS | TC33X-2-503E | VR2 | 1 | 50k trim, 100mW, 1 turn | SMD | Stair (https://uk.farnell.com/bourns/tc33x-2-503e/trimmer-pot-50k-25-1turn-smd/dp/1689867?st=TC33X-2-503E)
Zener Diode | LINEAR TECHNOLOGY | LT1004-CZ1.2 | D1 | 1 | 1.225V reference, 10µA | TH | Fair (https://uk.farnell.com/linear-technology/lt1004cz-1-2-pbf/voltage-ref-shunt-1-235v-to-226aa/dp/2115941?st=LT1004CZ)
Zener Diode | ON Semiconductor | LM385BZ-1.2G | D2 | 1 | 1.235V reference, 10µA | TH | Rare (https://uk.farnell.com/on-semiconductor/lm385bz-1-2g/voltage-ref-shunt-1-235v-to-226aa/dp/9664521?st=LM385BZ)
Zener Diode | MULTICOMP | 1N759A | D3 | 1 | 12V reference, 20mA | TH | Mare (https://uk.farnell.com/multicomp/1n759a/diode-zener-0-5w-12v-do-35/dp/1861493?st=1N759A)

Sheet: VoltageSourceBOM w changes
Bill of materials for Voltage Source (w/ resistance, Op amp & diode changes)
Part Name | Manufacturer | Manufacturer Part Number | PCB Reference | Qty | Description | SMD or TH | Link | Comment | Extra
Capacitor | EPCOS | B32529C1103J189 | C1 | 1 | 10nF, DC Film, 100V | TH | Here (https://uk.farnell.com/epcos/b32529c1103j189/cap-0-01-f-100v-5-pet/dp/2315548?st=B32529C1103J189) | 0805-10nF-50V, Ceramic, 10%, SMD, free | VJ0805Y103JXXPW1BC, MLCC, X7R, 10nF, 25V, 5%, SMD
Capacitor | Panasonic | ECW-FD2E475J | C2 | 1 | 4.7µF, DC Film, 450V | TH | Here (https://uk.farnell.com/panasonic/ecwfd2w475j/cap-4-7-f-450v-5-pp/dp/2805916?ost=ECW_FD2W475j&ddkey=https%3Aen-GB%2FElement14_Unit) | C0805X475K3RACAUTO, MLCC, 10%, X7R, 25V, SMD (can do 5% C0805X475J3RACAUTO)
Capacitor | Panasonic | ECW-FD2E105J | C3 | 1 | 1µF, DC Film, 450V | TH | There (https://uk.farnell.com/panasonic/ecwfd2w105j/cap-1-f-450v-5-pp/dp/2805908?st=ECW_FD2W105J) | C0805X105K3RACAUTO, MLCC, 10%, X7R, 25V, SMD (can do 5% C0805X105J3RACAUTO)
Capacitor | Vishay | VY2103M63Y5US6TV7 | C4 | 1 | 10nF, Ceramic, 20% tolerance | TH | Here (https://uk.rs-online.com/web/p/ceramic-single-layer-capacitors/7368928/) | 0805-10nF-50V, Ceramic, 10%, SMD, free | VJ0805Y103JXXPW1BC, MLCC, X7R, 10nF, 25V, 5%, SMD
Capacitor | KEMET | T491D106K025AT | C5 | 1 | 10µF, Tantalum, 25V, 10%, SMD | SMD | Here (https://www.digikey.co.uk/product-detail/en/kemet/T491D106K025AT/399-3765-1-ND/819090)
Screw Terminal | CAMDENBOSS | CTB500/2 | LED, Batt, DPDT-On-Off, Out | 4 | 2 pole, Screw | TH | Where (https://uk.farnell.com/camdenboss/ctb5000-2/terminal-block-wire-to-brd-2pos/dp/151789) | 1824747, 2 way, 5mm pitch, push-in spring connection, SMD, Horizontal, More expensive | 1824307, same as other SMD, vertical, More expensive
Screw Terminal | CAMDENBOSS | CTB500/3 | Potentiometer, DPDT-Voltage-Range | 2 | 3 pole, Screw | TH | Hare (https://uk.farnell.com/camdenboss/ctb5000-3/terminal-block-wire-to-brd-3pos/dp/151790?MER=bn_level5_5NP_EngagementRecSingleItem_1) | 1824750, 3 way, 5mm pitch, push-in spring connection, SMD, Horizontal, More expensive | 1824310, same as other SMD, vertical, More expensive
Op Amp | LINEAR TECHNOLOGY (Analog Devices) | LT6000IDCB#TRMPBF | U1 | 1 | 16µA, 18V supply, Low noise | SMD | Lair (https://www.mouser.co.uk/ProductDetail/Analog-Devices/LT6000IDCBTRMPBF)
Resistor | Panasonic | ERA6AEB474V | R1 | 1 | 470k, 0.1%, 25ppm, 0.125W, 0805, Thin film | SMD | Chair (https://uk.farnell.com/panasonic/era6aeb474v/res-470k-0-1-0-125w-0805-thin/dp/1577695?st=ERA6AEB474v) | 0805-470K, 100ppm, 1%,free
Resistor | Panasonic | ERA6AEB221V | R2 | 1 | 220R, 0.1%, 25ppm, 0.125W, 0805, Thin film | SMD | Tear (https://uk.farnell.com/panasonic/era6aeb221v/res-220r-0-1-0-125w-0805-thin/dp/1577649?st=ERA6AEB221v) | 0805-220R, 100ppm, 1%, free
Resistor | VISHAY | PNM0805E5001BST5 | R3, R6 | 2 | 5k, 0.1%, 25ppm, 0.2W, 0805, Thin Film | SMD | Eclair (https://www.mouser.co.uk/ProductDetail/Vishay-Thin-Film/PNM0805E5001BST5) | 0805-5K1, 5k1, 100ppm, 1%, free
Resistor | TE CONNECTIVITY | CPF-A-0805B1M0E1 | R4 | 1 | 1M, 0.1%, 25ppm, 0.1W, 0805, Thin film | SMD | Bear (https://uk.farnell.com/te-connectivity/cpf-a-0805b1m0e1/res-1m-0-1-0805-thin-film/dp/2483968?st=pansonic%20resistor%20080%201Mohm)
Resistor | Panasonic | MCU08050C1005FP500 | R5, R8 | 2 | 10M, 1%, 50ppm, 0.2W, 0805, Thin Film | SMD | Blair (https://www.mouser.co.uk/ProductDetail/Vishay-Beyschlag/MCU08050C1005FP500)
Resistor | Panasonic | ERA6AEB824V | R7 | 1 | 820k, 0.1%, 25ppm, 0.125W, 0805, Thin film | SMD | Bare (https://uk.farnell.com/panasonic/era6aeb824v/res-820k-0-1-0-125w-0805-thin/dp/1577698?st=ERA6AEB824v)
Resistor | TE CONNECTIVITY | CPF0805B2M0E | R9 | 1 | 2M, 0.1%, 25ppm, 0.1W, 0805, Thin film | SMD | Hair (https://www.mouser.co.uk/ProductDetail/TE-Connectivity-Holsworthy/CPF0805B2M0E)
Resistor | Panasonic | ERA6AEB3093V | R10 | 1 | 309k, 0.1%, 25ppm, 0.1W, 0805, Thin film | SMD | Stare (https://www.mouser.co.uk/ProductDetail/Panasonic/ERA-6AEB3093V)
Trimmer | BOURNS | TC33X-2-104E | VR1 | 1 | 100k trim, 25%, 250ppm, 100mW, 1 turn | SMD | Wear (https://uk.farnell.com/bourns/tc33x-2-104e/trimmer-100k-3mm/dp/1689864?st=TC33X-2-104E)
Trimmer | BOURNS | TC33X-2-503E | VR2 | 1 | 50k trim, 25%, 250ppm, 100mW, 1 turn | SMD | Stair (https://uk.farnell.com/bourns/tc33x-2-503e/trimmer-pot-50k-25-1turn-smd/dp/1689867?st=TC33X-2-503E)
Zener Diode | LINEAR TECHNOLOGY | LT1004CZ-1.2#PBF | D1 | 1 | 1.225V reference, 10µA | TH | Fair (https://uk.farnell.com/linear-technology/lt1004cz-1-2-pbf/voltage-ref-shunt-1-235v-to-226aa/dp/2115941?st=LT1004CZ) | LT1004CS8-1.2#PBF SMD version by same company, same spec, S8 package
Zener Diode | ON Semiconductor | LM385BZ-1.2G | D2 | 1 | 1.235V reference, 10µA | TH | Rare (https://uk.farnell.com/on-semiconductor/lm385bz-1-2g/voltage-ref-shunt-1-235v-to-226aa/dp/9664521?st=LM385BZ) | LM385BD-1.2G SMD version by same company, same spec, SOIC-8 package
Zener Diode | MULTICOMP | 1N759A | D3 | 1 | 12V reference, 20mA | TH | Mare (https://uk.farnell.com/multicomp/1n759a/diode-zener-0-5w-12v-do-35/dp/1861493?st=1N759A) | BZX84-C12.215, SMD (SOT23), free
Diode | Diodes Incorporated | 1N4148W-7-F | D4 - D9 | 6 | 0.6V for low current, 100V breakdown | SMD | Care (https://www.digikey.co.uk/product-detail/en/diodes-incorporated/1N4148W-7-F/1N4148W-FDICT-ND/815280) | 1N4148W-7-F, SMD, free

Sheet: LEDIndicatorBOM
Bill of materials for LED Indicator Circuit
Part Name | Manufacturer | Manufacturer Part Number | PCB Reference | Qty | Description | SMD or TH | Link | Comment | Extra
Screw Terminal | CAMDENBOSS | CTB500/2 | BatteryBus, LED1 - 5 | 6 | 2 pole, Screw | TH | Where (https://uk.farnell.com/camdenboss/ctb5000-2/terminal-block-wire-to-brd-2pos/dp/151789)
Zener Diode | ON Semiconductor | 1N5347BG | D1 | 1 | 10V reference | TH | Here (https://uk.farnell.com/on-semiconductor/1n5347bg/diode-zener-10v-5w/dp/9558055?st=zener%20diode%2010V) | Free SMD: BZX84-C10,215, 10V
Quad Comparator | ON Semiconductor | LM339AM | U1 | 1 | 36V supply, Low supply drain current | SMD | Here (https://www.digikey.co.uk/product-detail/en/on-semiconductor/LM339AM/LM339AMFS-ND/1051433)
Resistor | Panasonic | ERA-6AEB681V | R1 | 1 | 680R, Thin Film, 0.125W, 0805 | SMD | Here (https://www.mouser.co.uk/ProductDetail/Panasonic/ERA-6AEB681V) | 0805-680R, 0.125W, 100ppm, 1%, free
Resistor | Panasonic | ERA-6AEB332V | R2 | 1 | 3k3, Thin Film, 0.125W, 0805 | SMD | Here (https://www.mouser.co.uk/ProductDetail/Panasonic/ERA-6AEB332V) | 0805-3K3, 0.125W, 100ppm, 1%, free
Resistor | Panasonic | ERA-6AEB823V | R4 | 1 | 82k, Thin Film, 0.125W, 0805 | SMD | Here (https://www.mouser.co.uk/ProductDetail/Panasonic/ERA-6AEB823V) | 0805-82K, 0.125W, 100ppm, 1%, free
Trimmer | ? | ? | R3 | 1 | 12k | TH | ?
Resistor | Panasonic | ERA-6AEB473V | R5, R7, R8, R9, R11 | 5 | 47k, Thin Film, 0.125W, 0805 | SMD | Here (https://www.mouser.co.uk/ProductDetail/Panasonic/ERA-6AEB473V) | 0805-47K, 0.125W, 100ppm, 1%, free
Resistor | Panasonic | ERA-6AEB433V | R6 | 1 | 43k, Thin Film, 0.125W, 0805 | SMD | Here (https://www.mouser.co.uk/ProductDetail/Panasonic/ERA-6AEB433V) | 0805-43K, 0.125W, 100ppm, 1%, free
Resistor | Panasonic | ERA-6AEB683V | R12 | 1 | 68k, Thin Film, 0.125W, 0805 | SMD | Here (https://www.mouser.co.uk/ProductDetail/Panasonic/ERA-6AEB683V) | 0805-68K, 0.125W, 100ppm, 1%, free
Resistor | Panasonic | ERA-6AEB563V | R10 | 1 | 56k, Thin Film, 0.125W, 0805 | SMD | Here (https://www.mouser.co.uk/ProductDetail/Panasonic/ERA-6AEB563V) | 0805-56K, 0.125W, 100ppm, 1%, free
Resistor | Panasonic | ERA-6AEB102V | R13 - R17 | 5 | 1k, Thin Film, 0.125W, 0805 | SMD | Here (https://www.mouser.co.uk/ProductDetail/Panasonic/ERA-6AEB102V) | 0805-1K, 0.125W, 100ppm, 1%, free
Capacitor | Vishay | VY2103M63Y5US6TV7 | C1 | 1 | 10nF, Ceramic, 20% tolerance | TH | Here (https://uk.rs-online.com/web/p/ceramic-single-layer-capacitors/7368928/) | 0805-10nF-50V, Ceramic, 10%, SMD, free | VJ0805Y103JXXPW1BC, MLCC, X7R, 10nF, 25V, 5%, SMD

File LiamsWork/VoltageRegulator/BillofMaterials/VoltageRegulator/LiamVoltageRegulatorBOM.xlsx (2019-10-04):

Bill of materials for Voltage Regulator PCB
Part Name | Manufacturer | Manufacturer Part Number | PCB Reference | Qty | Description | SMD, TH or Other (BGA, QFN etc.) | Link
0805 Capacitor | PCB Train free component stock | 0805-10nF-50V | C1 | 1 | CAPACITOR; 10nF; 0805; 50V; 10%; X7R; -55+125C | SMD
0805 Capacitor | TDK | C2012X7R1E475K125AB | C2 | 1 | 0805; 4.7µF; MLCC; X7R; 25V; 10% | SMD | Farnell (https://uk.farnell.com/tdk/c2012x7r1e475k125ab/cap-4-7-f-25v-10-x7r-0805/dp/2346943)
0805 Capacitor | KEMET | C0805X105K3RACAUTO | C3 | 1 | 0805; 1µF; MLCC; X7R; 25V; 10% | SMD | Farnell (https://uk.farnell.com/kemet/c0805x105k3racauto/cap-1-f-25v-10-x7r-0805/dp/2478267?st=C0805X105K3RACAUTO)
0805 Capacitor | Vishay | VJ0805Y103JXXPW1BC | C4 | 1 | 0805; 10nF; MLCC; X7R; 25V; 5% | SMD | Farnell (https://uk.farnell.com/vishay/vj0805y103jxxpw1bc/cap-0-01-f-25v-5-x7r-0805/dp/2896555?st=VJ0805Y103JXXPW1BC) | Mouser (https://www.mouser.co.uk/ProductDetail/Vishay-Vitramon/VJ0805Y103JXXPW1BC?qs=9AX3phJxokVo8tzHKFx3bA==)
0805 Capacitor | KEMET | T491D106K025AT | C5 | 1 | 0805; 10µF; Tantalum; 25V; 10% | SMD | Farnell (https://uk.farnell.com/kemet/t491d106k025at/cap-10-f-25v-10-2917-smd/dp/1457490?st=T491D106K025AT) | Digikey (https://www.digikey.co.uk/product-detail/en/kemet/T491D106K025AT/399-3765-1-ND/819090)
Screw Terminal | CAMDENBOSS | CTB5000/2 | LED, BATTERY, DPDT-ON-OFF, OUTPUT | 4 | 2 Pole, Screw-in | TH | Farnell (https://uk.farnell.com/camdenboss/ctb5000-2/terminal-block-wire-to-brd-2pos/dp/151789)
Screw Terminal | CAMDENBOSS | CTB5000/3 | POTENTIOMETER, DPDT-VOLTAGE-RANGE | 2 | 3 Pole, Screw | TH | Farnell (https://uk.farnell.com/camdenboss/ctb5000-3/terminal-block-wire-to-brd-3pos/dp/151790?MER=bn_level5_5NP_EngagementRecSingleItem_1)
Op Amp | LINEAR TECHNOLOGY | LT1494CS8#PBF | U1 | 1 | 1.5µA Max, 36V supply, Low noise | SMD | RS Components (https://uk.rs-online.com/web/p/op-amps/7799306/) | Mouser (https://www.mouser.co.uk/ProductDetail/Analog-Devices/LT1494CS8PBF)
0805 Resistor | PCB Train free component stock | 0805-470K | R1 | 1 | RESISTOR; 0805; 0.125W; 470k; 100ppm; 1%; 150V; -55+125C | SMD
0805 Resistor | PCB Train free component stock | 0805-220R | R2 | 1 | RESISTOR; 0805; 0.125W; 220R; 100ppm; 1%; 150V; -55+125C | SMD
0805 Resistor | PCB Train free component stock | 0805-5K1 | R3, R6 | 2 | RESISTOR; 0805; 0.125W; 5k1; 100ppm; 1%; 150V; -55+125C | SMD
Resistor | TE CONNECTIVITY | CPF-A-0805B1M0E1 | R4 | 1 | 1M, 0.1%, 25ppm, 0.1W, 0805, Thin film | SMD | Farnell (https://uk.farnell.com/te-connectivity/cpf-a-0805b1m0e1/res-1m-0-1-0805-thin-film/dp/2483968?st=pansonic%20resistor%20080%201Mohm)
Resistor | Panasonic | MCU08050C1005FP500 | R5, R8 | 2 | 10M, 1%, 50ppm, 0.2W, 0805, Thin Film | SMD |  | Mouser (https://www.mouser.co.uk/ProductDetail/Vishay-Beyschlag/MCU08050C1005FP500)
Resistor | Panasonic | ERA6AEB824V | R7 | 1 | 820k, 0.1%, 25ppm, 0.125W, 0805, Thin film | SMD | Farnell (https://uk.farnell.com/panasonic/era6aeb824v/res-820k-0-1-0-125w-0805-thin/dp/1577698?st=ERA6AEB824v)
Resistor | TE CONNECTIVITY | CPF0805B2M0E | R9 | 1 | 2M, 0.1%, 25ppm, 0.1W, 0805, Thin film | SMD | Farnell (https://uk.farnell.com/te-connectivity/cpf0805b2m0e1/res-2m0-0-1-0-1w-0805-thin-film/dp/2616188?ost=CPF0805B2M0E) | Mouser (https://www.mouser.co.uk/ProductDetail/TE-Connectivity-Holsworthy/CPF0805B2M0E)
Resistor | Panasonic | ERA6AEB3093V | R10 | 1 | 309k, 0.1%, 25ppm, 0.1W, 0805, Thin film | SMD | Farnell (https://uk.farnell.com/panasonic/era6aeb3093v/resistor-0805-309k-full-reel/dp/1811183?st=ERA-6AEB3093V) | Mouser (https://www.mouser.co.uk/ProductDetail/Panasonic/ERA-6AEB3093V)
Trimmer | BOURNS | TC33X-2-104E | VR1 | 1 | 100k trim, 25%, 250ppm, 100mW, 1 turn | SMD | Farnell (https://uk.farnell.com/bourns/tc33x-2-104e/trimmer-100k-3mm/dp/1689864?st=TC33X-2-104E)
Trimmer | BOURNS | TC33X-2-503E | VR2 | 1 | 50k trim, 25%, 250ppm, 100mW, 1 turn | SMD | Farnell (https://uk.farnell.com/bourns/tc33x-2-503e/trimmer-pot-50k-25-1turn-smd/dp/1689867?st=TC33X-2-503E)
Micropower voltage reference 1.225V | LINEAR TECHNOLOGY | LT1004CS8-1.2#PBF | D1 | 1 | 1.225V reference, 10µA | SMD | RS Components (https://uk.rs-online.com/web/p/voltage-references/7617905/) | Mouser (https://www.mouser.co.uk/ProductDetail/Analog-Devices/LT1004CS8-12PBF)
Micropower voltage reference 1.235V | ON Semiconductor | LM385BD-1.2G | D2 | 1 | 1.235V reference, 10µA | SMD | Farnell (https://uk.farnell.com/on-semiconductor/lm385bd-1-2g/voltage-ref-shunt-1-235v-nsoic/dp/2318566?ost=LM385BD-1.2G) | Mouser (https://www.mouser.co.uk/ProductDetail/ON-Semiconductor/LM385BD-12G?qs=2OtswVQKCOGKPjy80YuMAg%3D%3D)
Zener Diode | PCB Train free component stock | BZX84-C12.215 | D3 | 1 | DIODE, ZENER, 12V, 0.25W, SOT23 | SMD

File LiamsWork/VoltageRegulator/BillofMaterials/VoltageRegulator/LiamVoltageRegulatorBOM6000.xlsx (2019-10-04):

Bill of materials for Voltage Regulator PCB
Part Name | Manufacturer | Manufacturer Part Number | PCB Reference | Qty | Description | SMD, TH or Other (BGA, QFN etc.) | Comment
0805 Capacitor | PCB Train free component stock | 0805-10nF-50V | C1 | 1 | CAPACITOR; 10nF; 0805; 50V; 10%; X7R; -55+125C | SMD
0805 Capacitor | KEMET | C0805X475J3RACAUTO | C2 | 1 | 0805; 4.7µF; MLCC; X7R; 25V; 5% | SMD
0805 Capacitor | KEMET | C0805X105J3RACAUTO | C3 | 1 | 0805; 1µF; MLCC; X7R; 25V; 5% | SMD
0805 Capacitor | Vishay | VJ0805Y103JXXPW1BC | C4 | 1 | 0805; 10nF; MLCC; X7R; 25V; 5% | SMD
0805 Capacitor | KEMET | T491D106K025AT | C5 | 1 | 0805; 10µF; Tantalum; 25V; 10% | SMD
Screw Terminal | CAMDENBOSS | CTB5000/2 | LED, BATTERY, DPDT-ON-OFF, OUTPUT | 4 | 2 Pole, Screw-in | TH
Screw Terminal | CAMDENBOSS | CTB5000/3 | POTENTIOMETER, DPDT-VOLTAGE-RANGE | 2 | 3 Pole, Screw | TH
Op Amp | LINEAR TECHNOLOGY (Analog Devices) | LT6000IDCB#TRMPBF | U1 | 1 | 16µA max, 16V supply, Low noise | QFN
0805 Resistor | PCB Train free component stock | 0805-470K | R1 | 1 | RESISTOR; 0805; 0.125W; 470k; 100ppm; 1%; 150V; -55+125C | SMD
0805 Resistor | PCB Train free component stock | 0805-220R | R2 | 1 | RESISTOR; 0805; 0.125W; 220R; 100ppm; 1%; 150V; -55+125C | SMD
0805 Resistor | PCB Train free component stock | 0805-5K1 | R3, R6 | 2 | RESISTOR; 0805; 0.125W; 5k1; 100ppm; 1%; 150V; -55+125C | SMD
Resistor | TE CONNECTIVITY | CPF-A-0805B1M0E1 | R4 | 1 | 1M, 0.1%, 25ppm, 0.1W, 0805, Thin film | SMD
Resistor | Panasonic | MCU08050C1005FP500 | R5, R8 | 2 | 10M, 1%, 50ppm, 0.2W, 0805, Thin Film | SMD
Resistor | Panasonic | ERA6AEB824V | R7 | 1 | 820k, 0.1%, 25ppm, 0.125W, 0805, Thin film | SMD
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

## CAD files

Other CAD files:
LiamsWork/AmplifierPowerSupply/InventorFiles/AmplifierPowerSupplyNew.dwg
LiamsWork/StripLineFilter/NewSinkV2.dwg
LiamsWork/StripLineFilter/NewSink.dwg
LiamsWork/StripLineFilter/NewSinkFINAL.dwg
LiamsWork/StripLineFilter/NewSinkV3.dwg
LiamsWork/StripLineFilter/OldVersions/NewSinkV4.0005.dwg
LiamsWork/StripLineFilter/OldVersions/NewSinkV3.0002.dwg
LiamsWork/StripLineFilter/OldVersions/NewSink.0002.dwg
LiamsWork/AmplifierPowerSupply/InventorFiles/AmplifierPowerSupplyNew.ipt
LiamsWork/StripLineFilter/NewSink.ipt
LiamsWork/StripLineFilter/NewSinkFINAL.ipt
LiamsWork/StripLineFilter/NewSinkV2.ipt
LiamsWork/StripLineFilter/NewSinkV3.ipt
LiamsWork/StripLineFilter/OldVersions/NewSink.0002.ipt
LiamsWork/StripLineFilter/OldVersions/NewSinkV2.0003.ipt
LiamsWork/StripLineFilter/OldVersions/NewSinkV3.0002.ipt
LiamsWork/StripLineFilter/OldVersions/NewSinkV4.0001.ipt

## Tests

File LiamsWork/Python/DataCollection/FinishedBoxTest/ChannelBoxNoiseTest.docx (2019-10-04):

I did 2 repeated tests for each voltage range, and measured the variation in the signal over a long time period.

Channel 2:

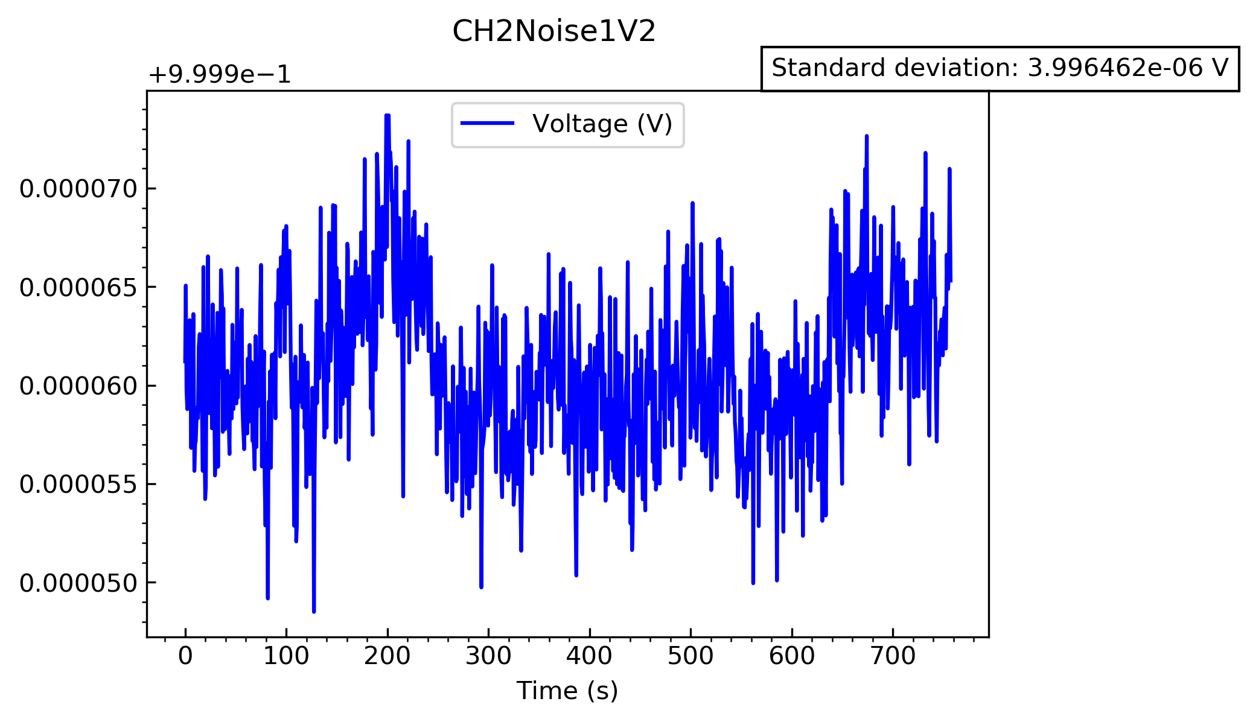
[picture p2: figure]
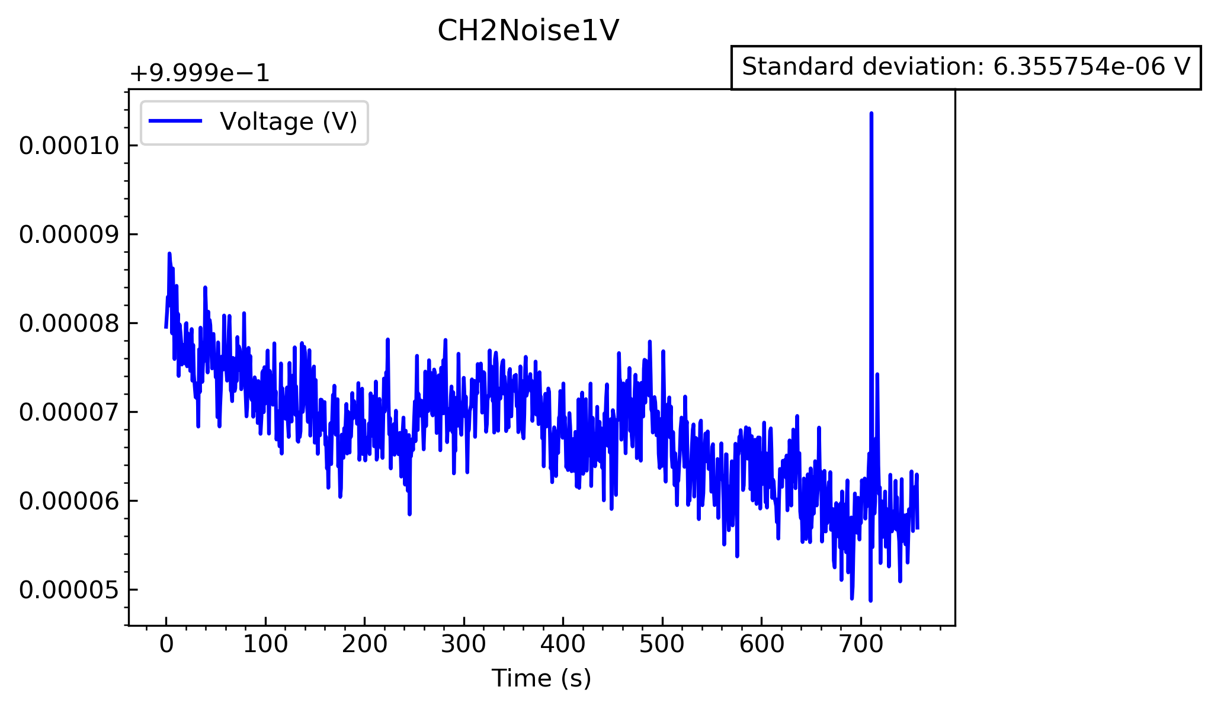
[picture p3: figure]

Look at the 1V range first

In the first test there is a clear decrease at the beginning, which may be due to the circuit just being switched to that range. I would consider the second test to be more accurate, which gives a standard deviation of 3.996x10⁻⁶V

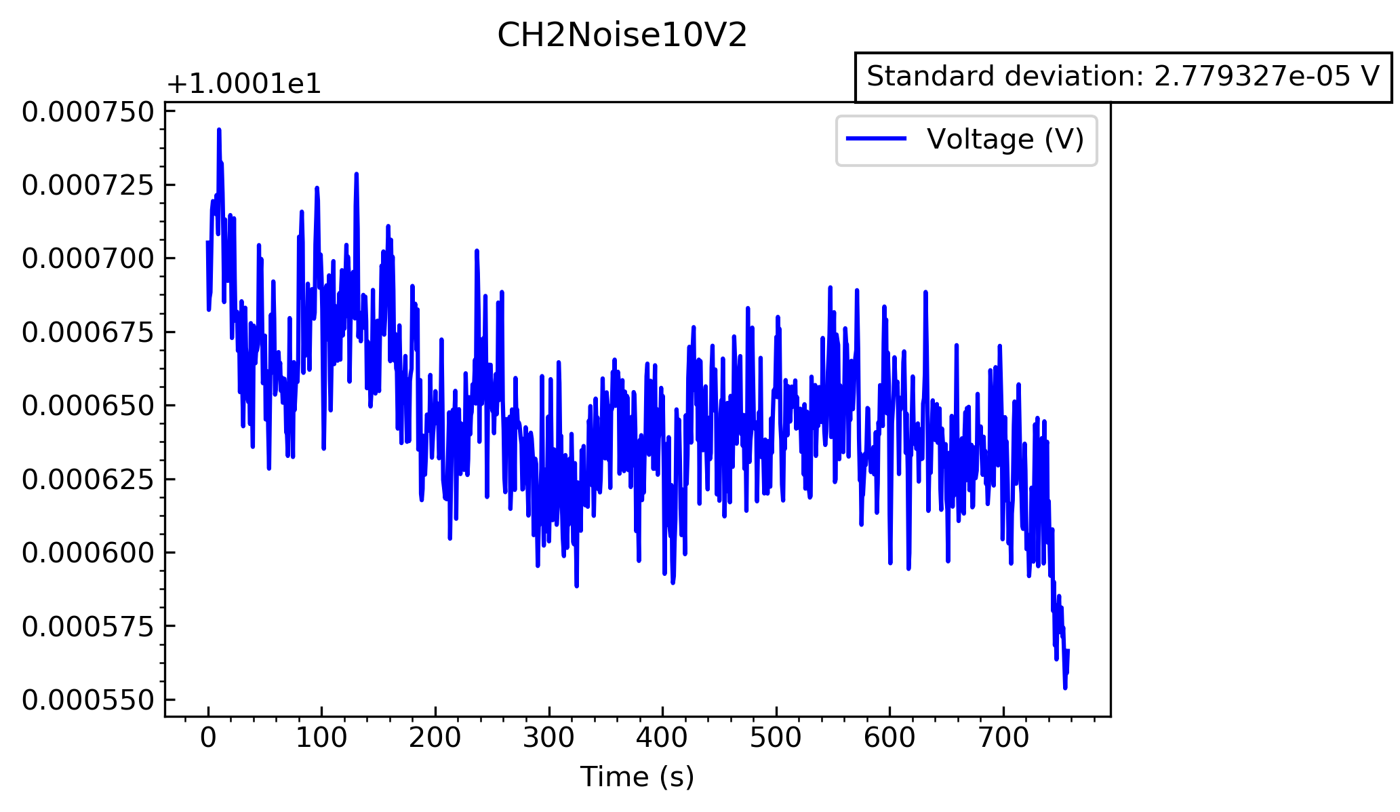
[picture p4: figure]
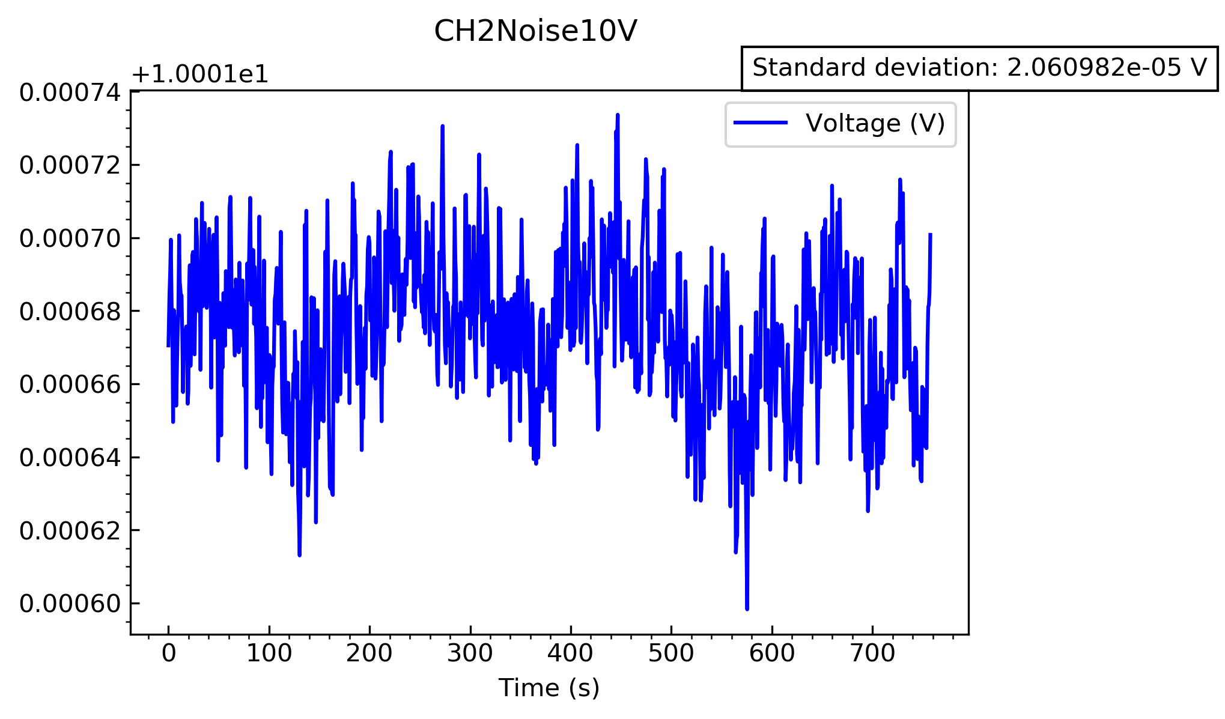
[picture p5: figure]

Now look at the 10V range

This time they are both very similar, however there is a decrease in the voltage signal at the end of the second test. I am unsure why this happened. In any case the standard deviations are larger than in the 1V case, which are 2.061x10⁻⁵ V and 2.779x10⁻⁵ V for the first and second test respectively.

Channel 7:

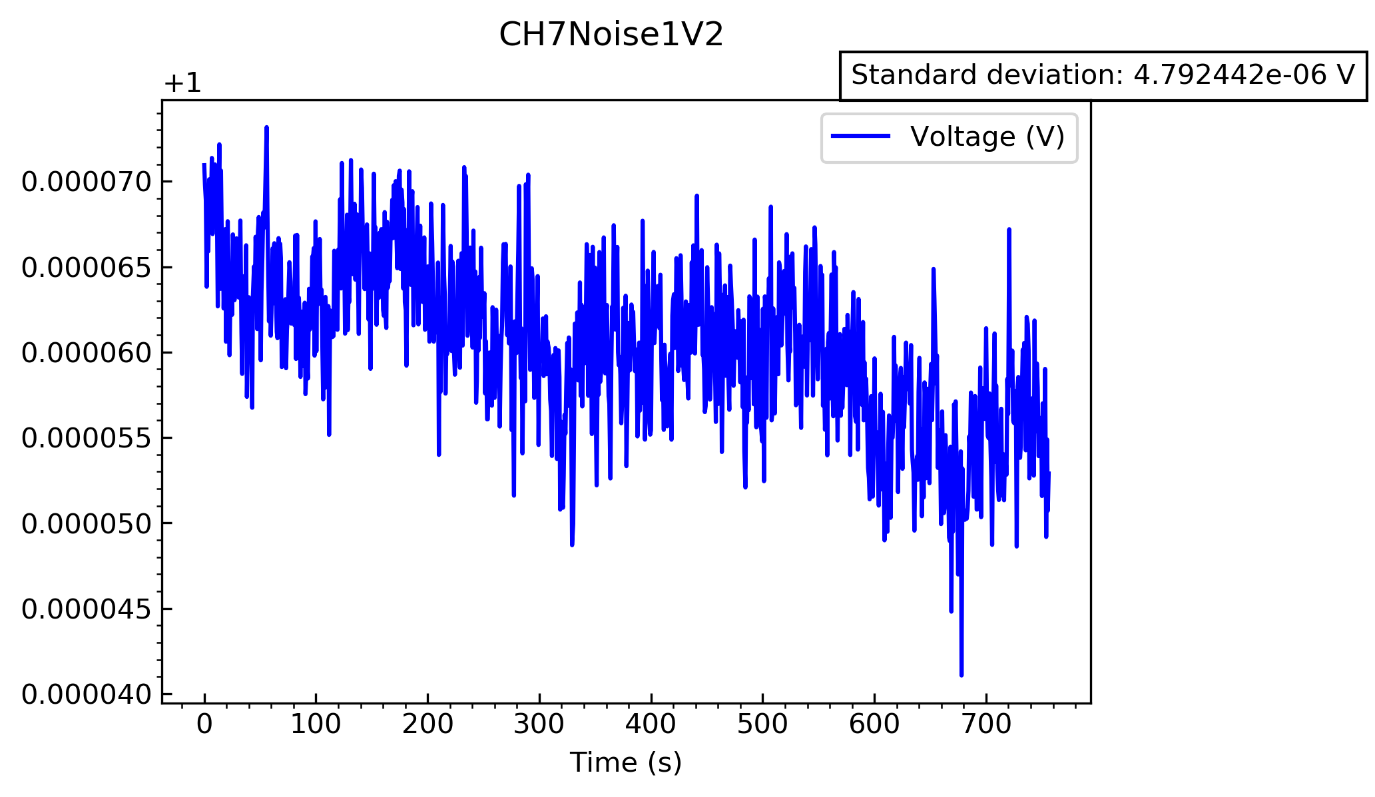
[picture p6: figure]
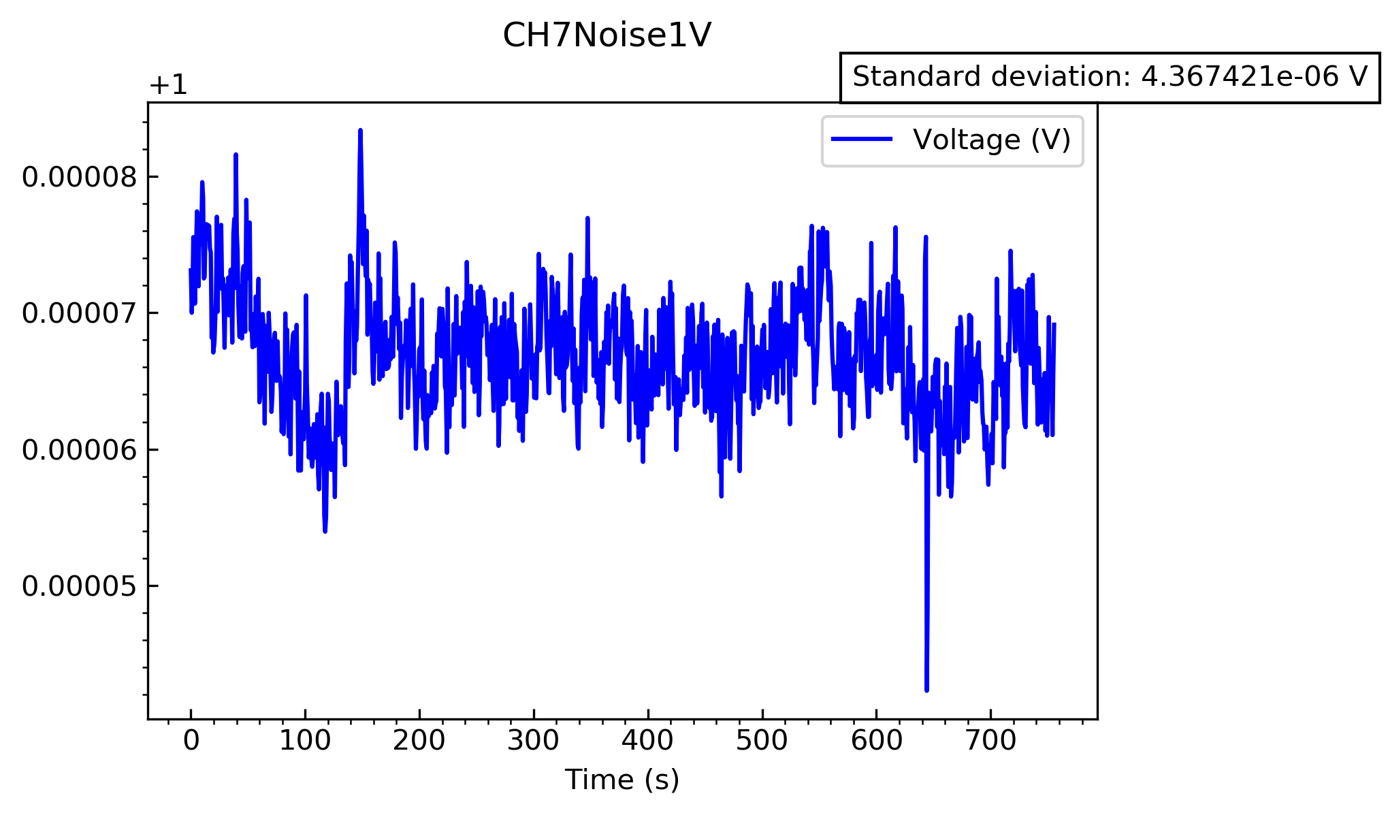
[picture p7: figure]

Look at the 1V range again:

There were some strange peaks in the first test, which I will assume is just random interference with nearby electronic devices. The standard deviations look very similar to before, however they are slightly larger, being 4.367x10⁻⁶ V and 4.792x10⁻⁶ V.

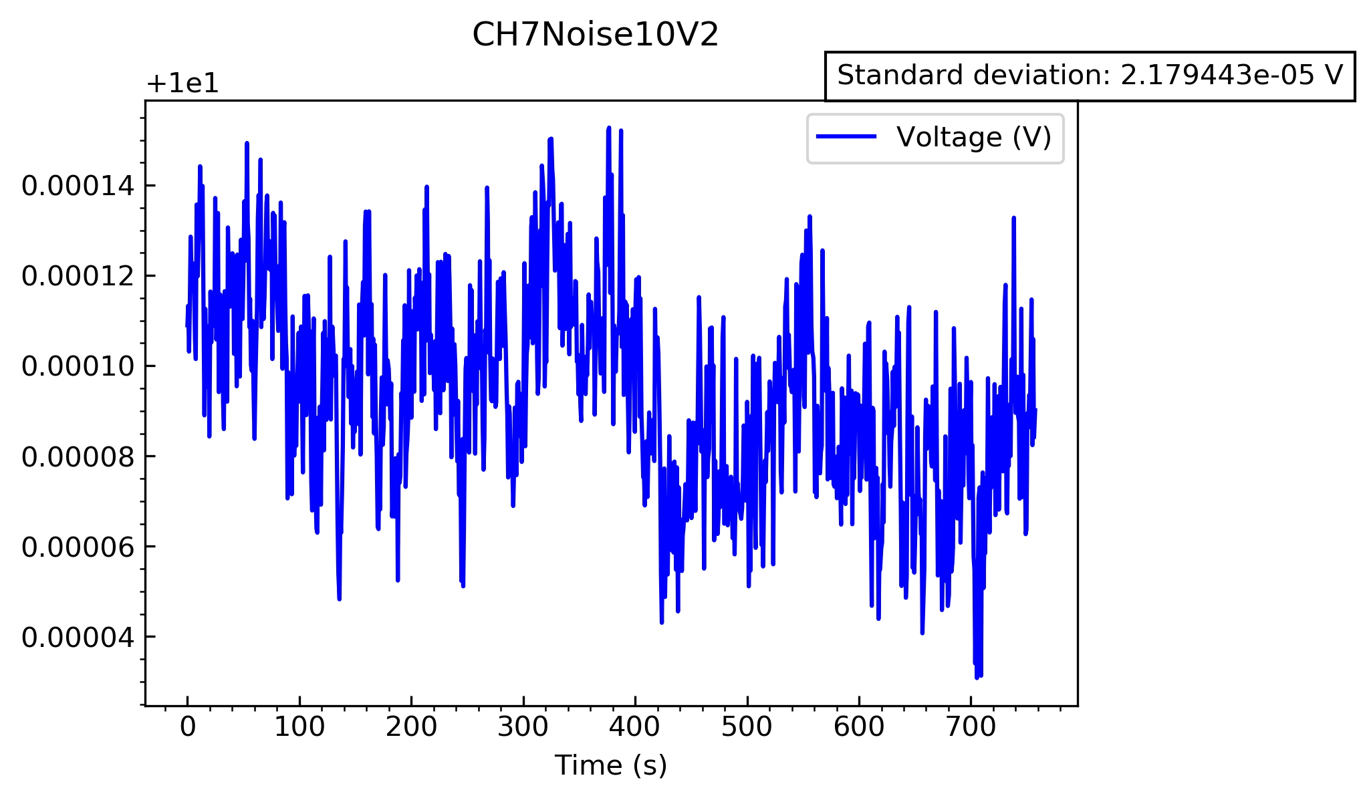
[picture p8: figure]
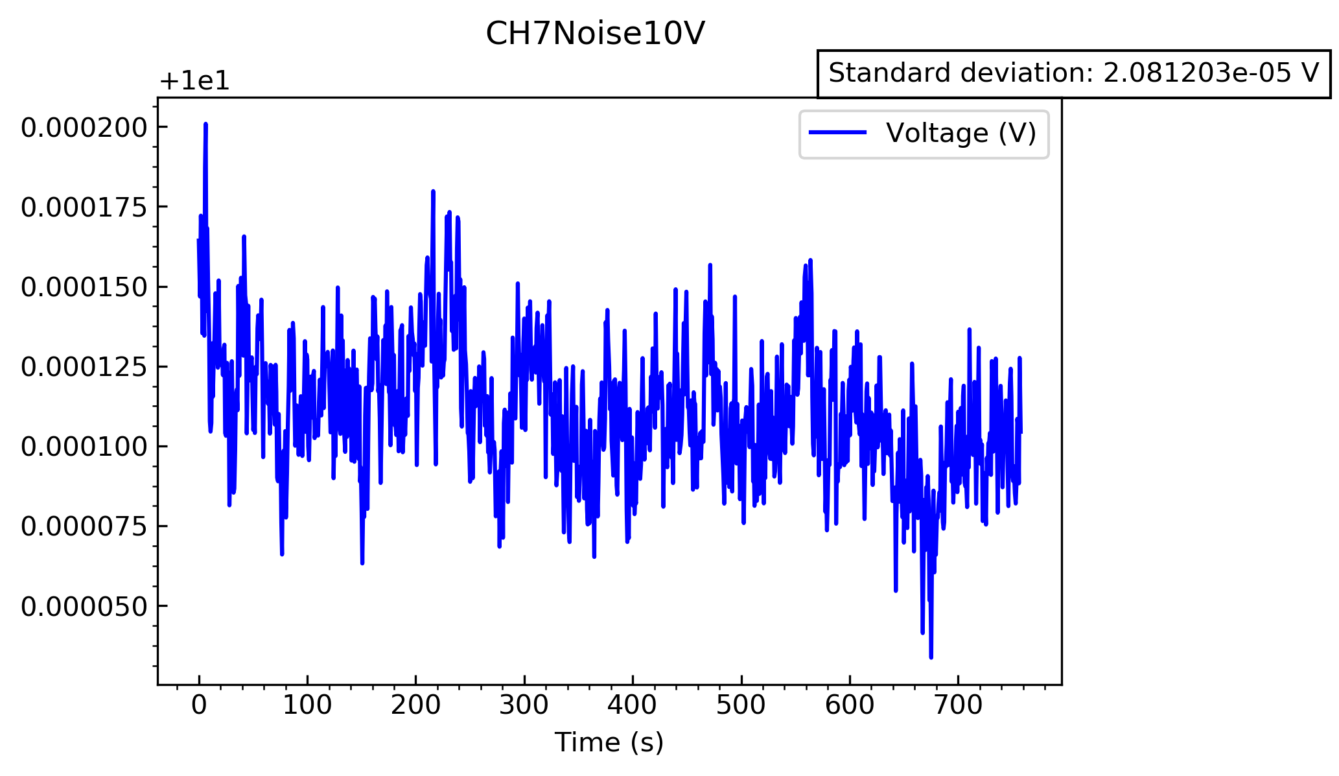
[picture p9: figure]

Again, look at the 10V range

These graphs look very similar, and have a similar standard deviation, showing that these are consistent. The standard deviations here are 2.081x10⁻⁵ V and 2.179x10⁻⁵ V for the first and second test respectively.

Channel 10:

Do the same again, looking at the 1V range first, and the 10V range afterwards.

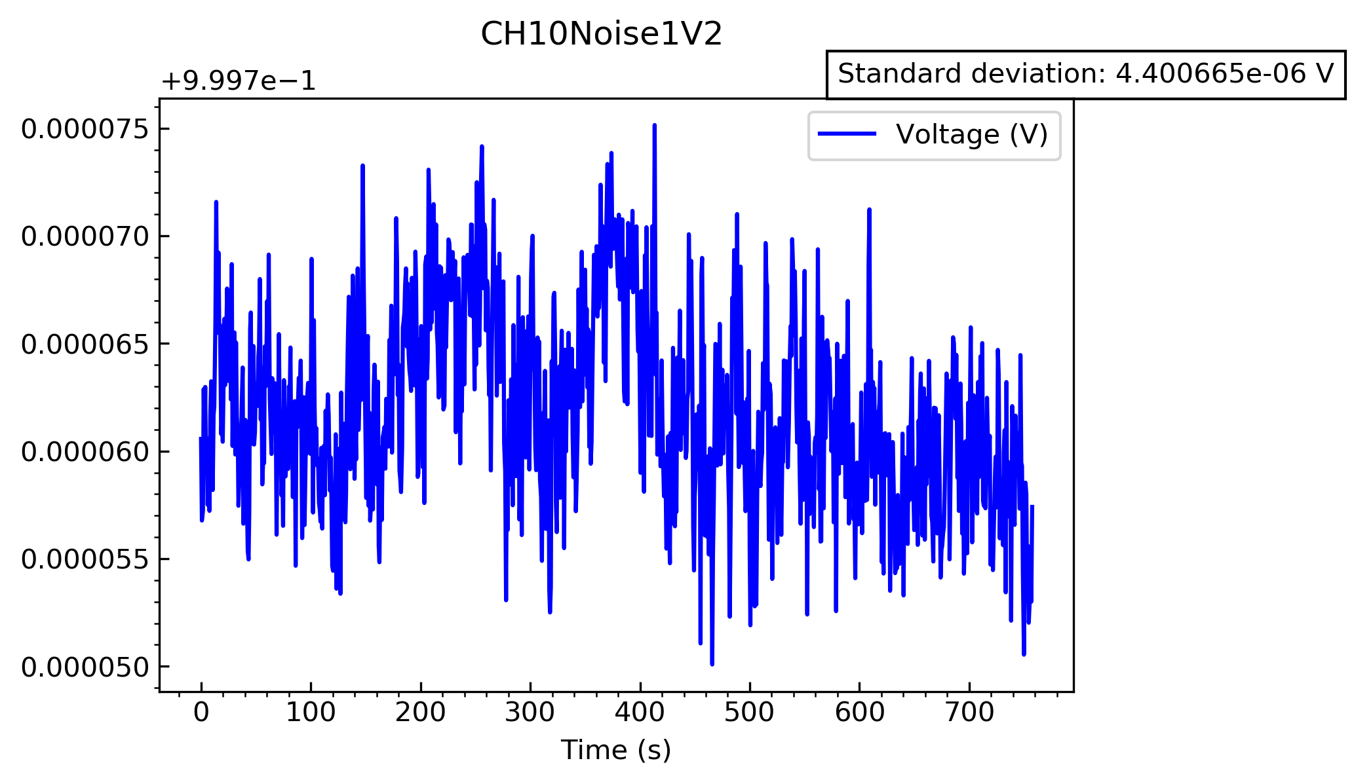
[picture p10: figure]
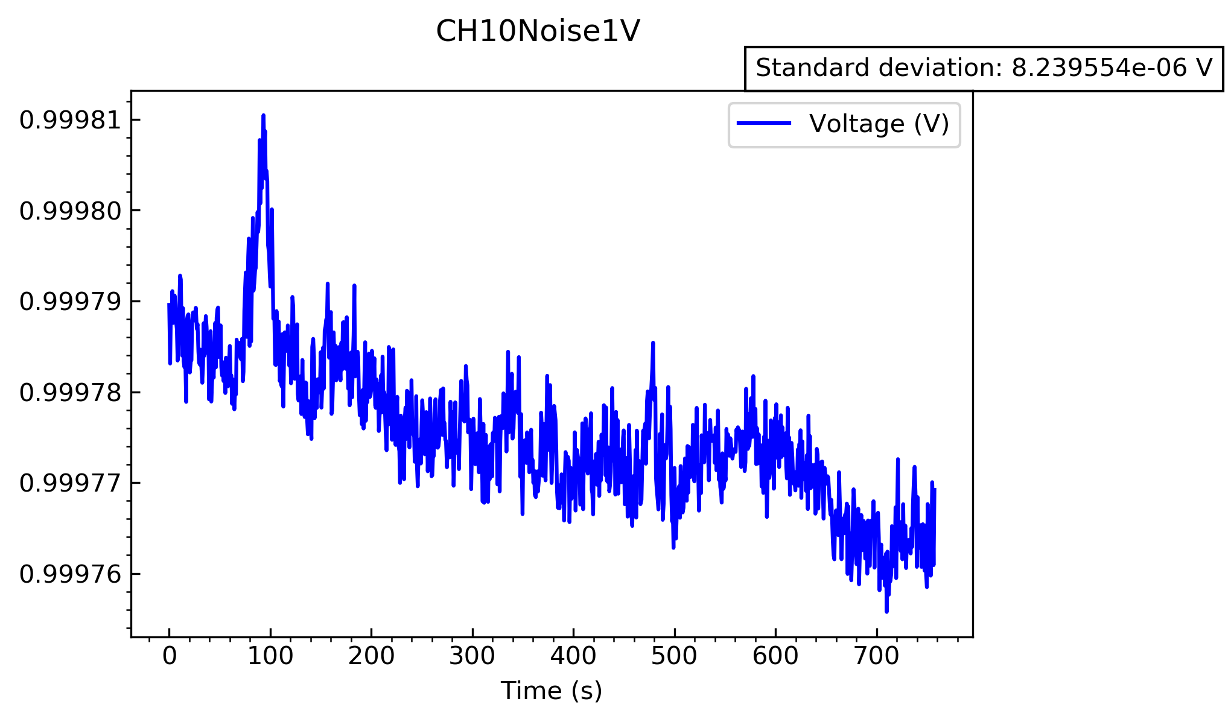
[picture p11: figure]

In the first test, there seems to be a clear decrease, and a large spike with a decent width. The decrease can be attributed to not enough time taken before starting the experiment and switching the range over. However, I am unsure where this thick peak has come from. Therefore, I will assume that the second experiment is more accurate, with a standard deviation of 4.401x10⁻⁶ V, which is similar to the other results obtained for this voltage range.


Both of these graphs both display some sort of gradual increase in the signal voltage, which is very interesting. I am, again, unsure about where this may have come from. The standard deviations for this test will be taken with a grain of salt, and I would like to perform this part of the experiment again to see whether this phenomena appears again in a third test.

Overall, of the channels tested, they all work very well, and all deviate minimally from the chosen voltage.

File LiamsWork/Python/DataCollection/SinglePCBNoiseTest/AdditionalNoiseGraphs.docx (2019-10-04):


These are the graphs to quantify the noise when the range was set to 1V without any shielding. The standard deviation for this ranged between 5.66x10⁻⁶ V and 6.47x10⁻⁶ V


These are the graphs for when the range is set to 10V, but the voltage has been dialled down to 1V. As is clear, the noise graphs are very similar, and both give very similar standard deviations.

Therefore, the additional noise seen at 10V must be due to the op amp itself

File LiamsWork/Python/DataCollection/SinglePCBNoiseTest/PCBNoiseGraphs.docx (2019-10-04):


DMM noise quantified. Looks correct, as the standard deviation is 1-2 orders of magnitude smaller

Both tests had one outlier, namely the 2nd test for 1V and the 1st test for 10V. This was due to the range being switched, and it being measured straight away. This was seen as a slow rise in voltage over 100-200s, which then levelled out.


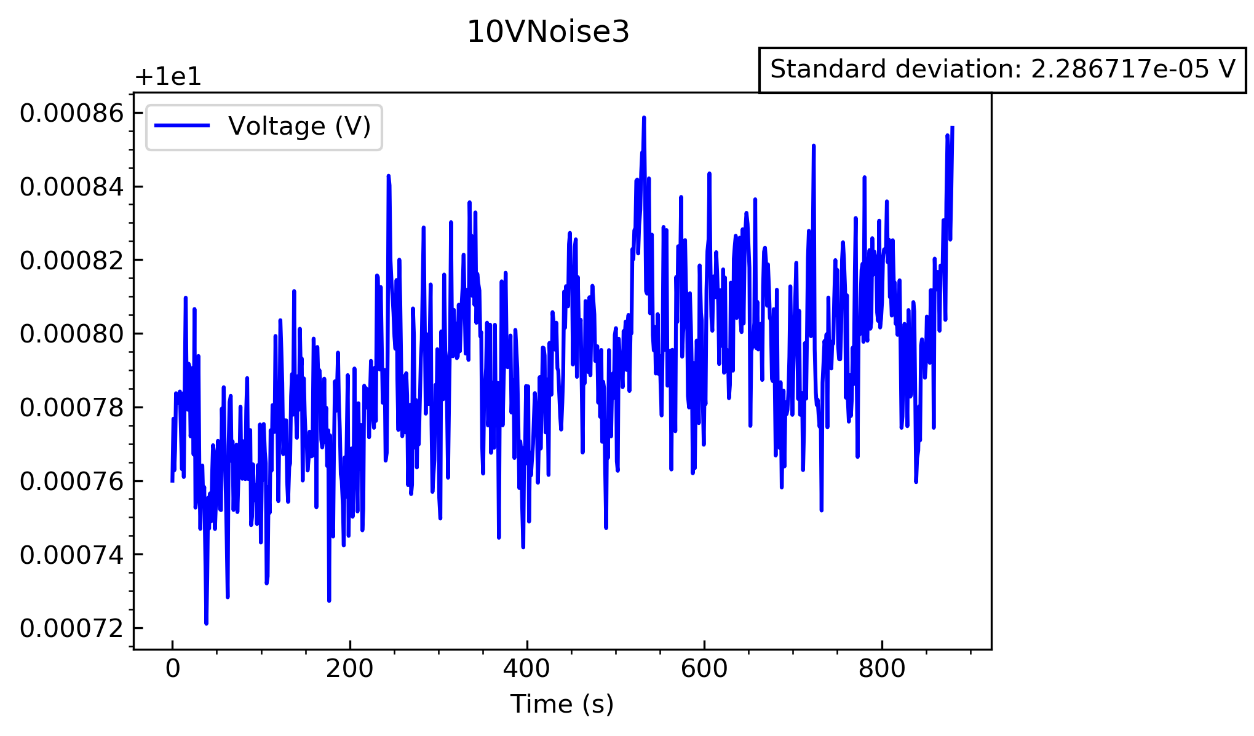
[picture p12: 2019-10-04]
LiamsWork/Python/DataCollection/SinglePCBNoiseTest/10VNoise3.png

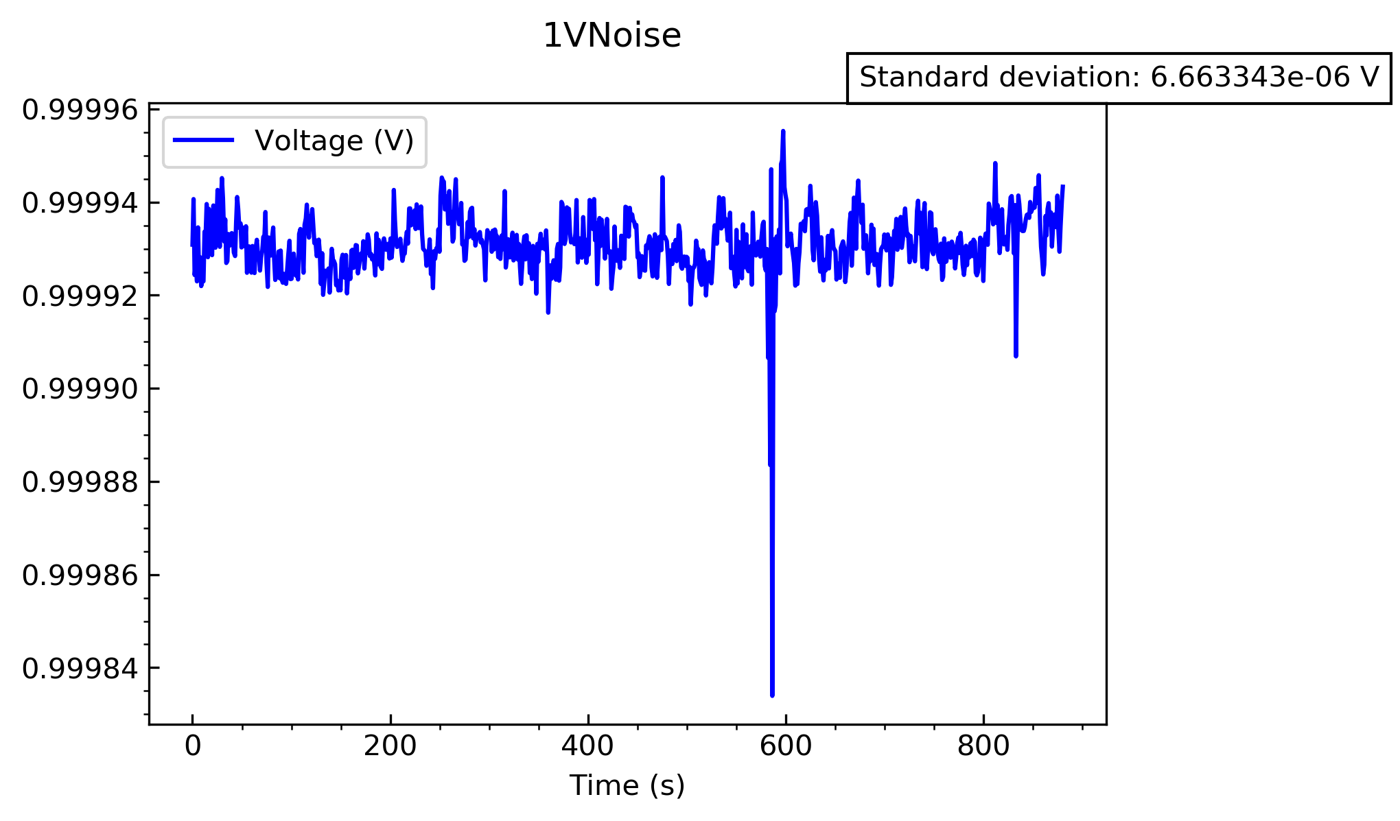
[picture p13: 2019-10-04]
LiamsWork/Python/DataCollection/SinglePCBNoiseTest/1VNoise.png

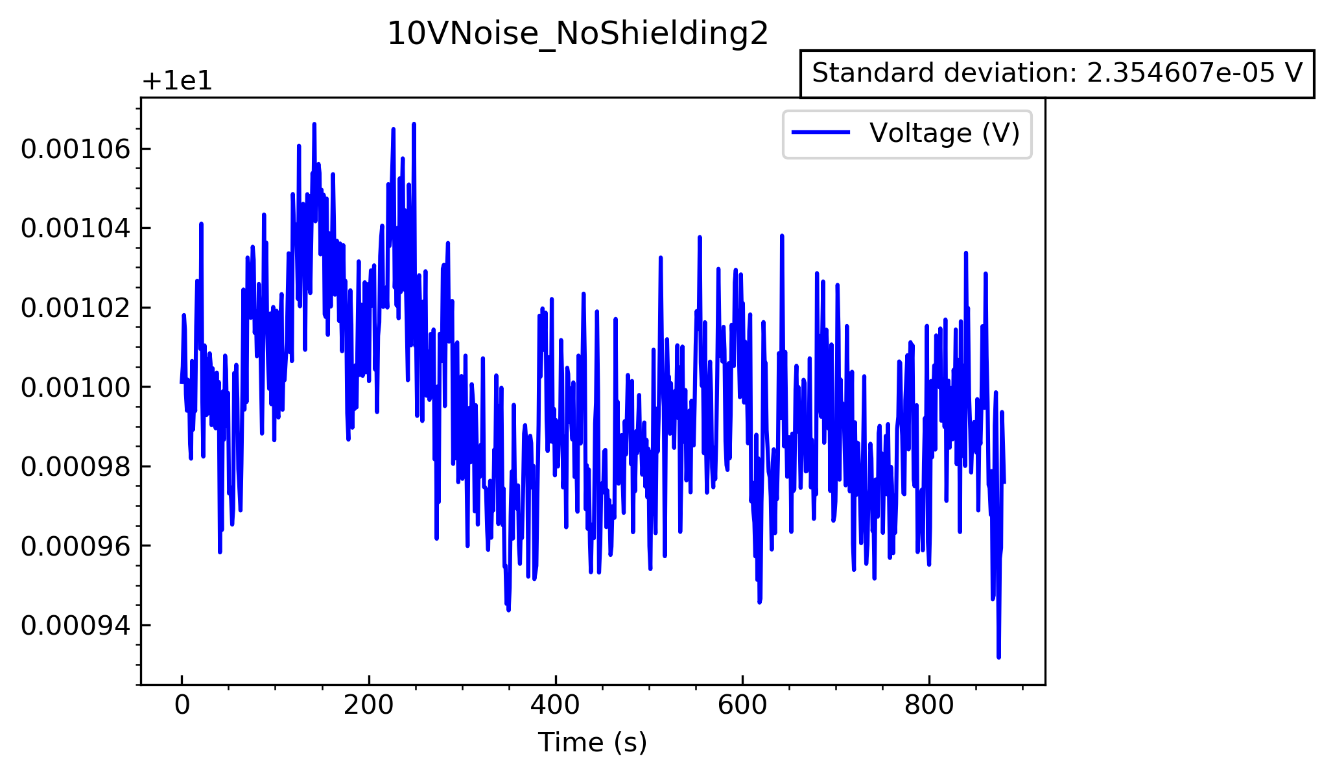
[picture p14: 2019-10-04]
LiamsWork/Python/DataCollection/SinglePCBNoiseTest/10VNoise_NoShielding2.png

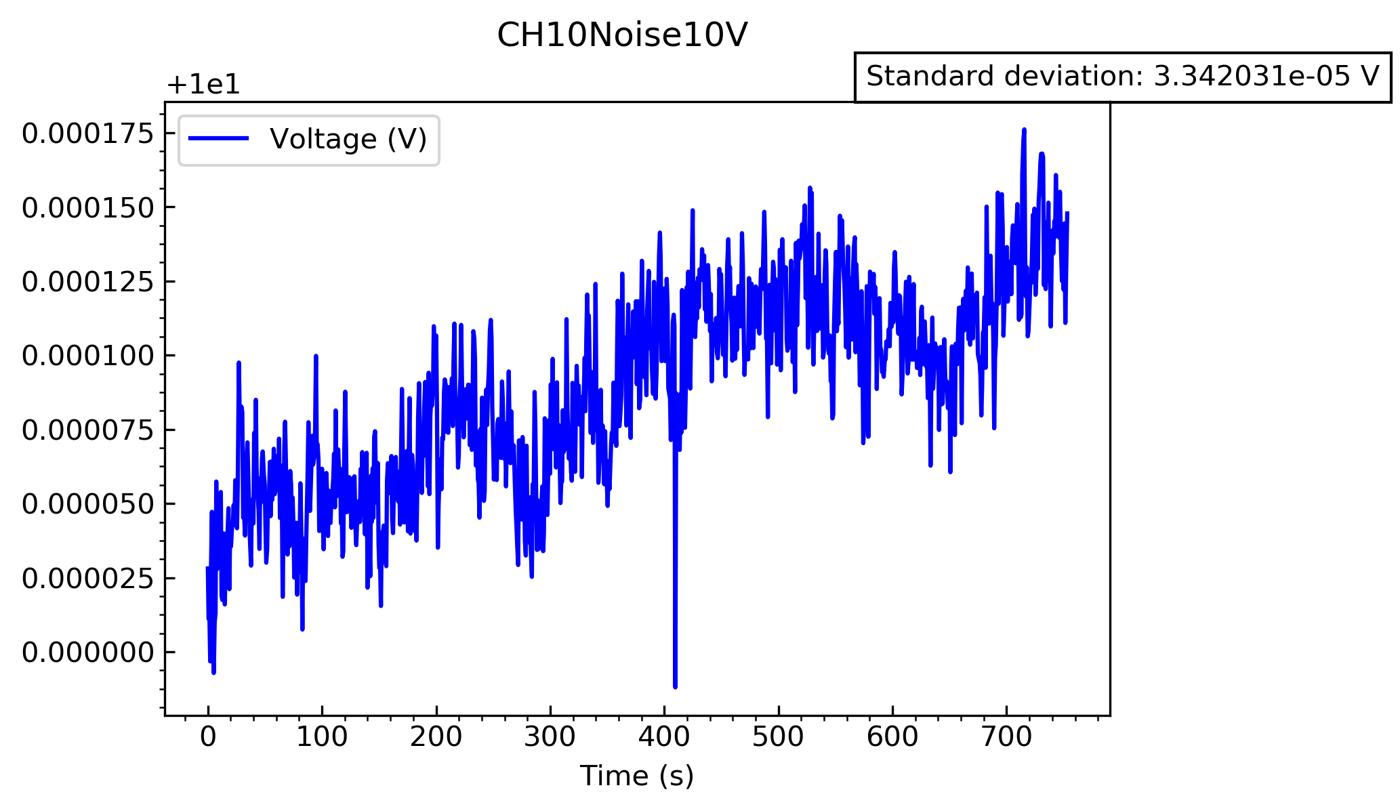
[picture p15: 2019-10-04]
LiamsWork/Python/DataCollection/FinishedBoxTest/CH10Noise10V.png

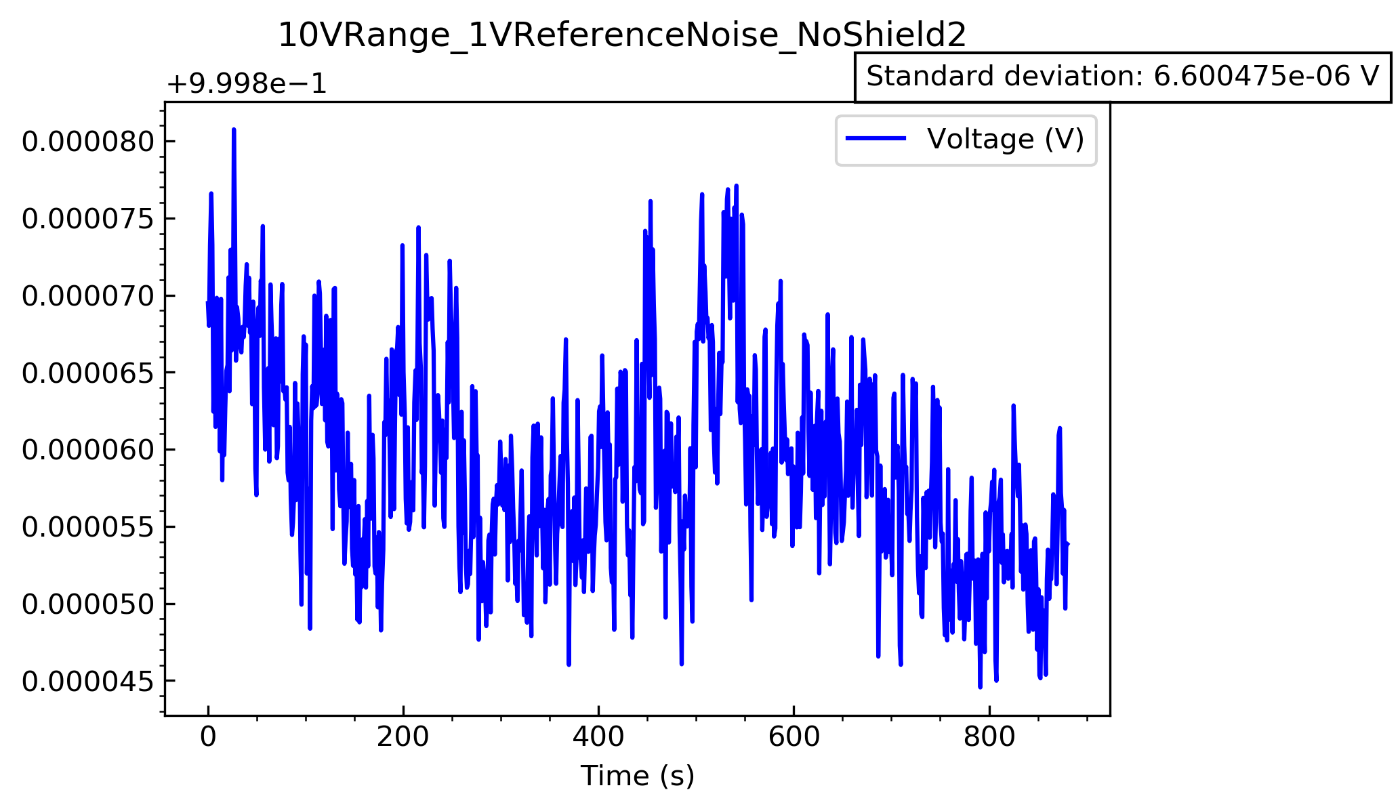
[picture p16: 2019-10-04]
LiamsWork/Python/DataCollection/SinglePCBNoiseTest/10VRange_1VReferenceNoise_NoShield2.png

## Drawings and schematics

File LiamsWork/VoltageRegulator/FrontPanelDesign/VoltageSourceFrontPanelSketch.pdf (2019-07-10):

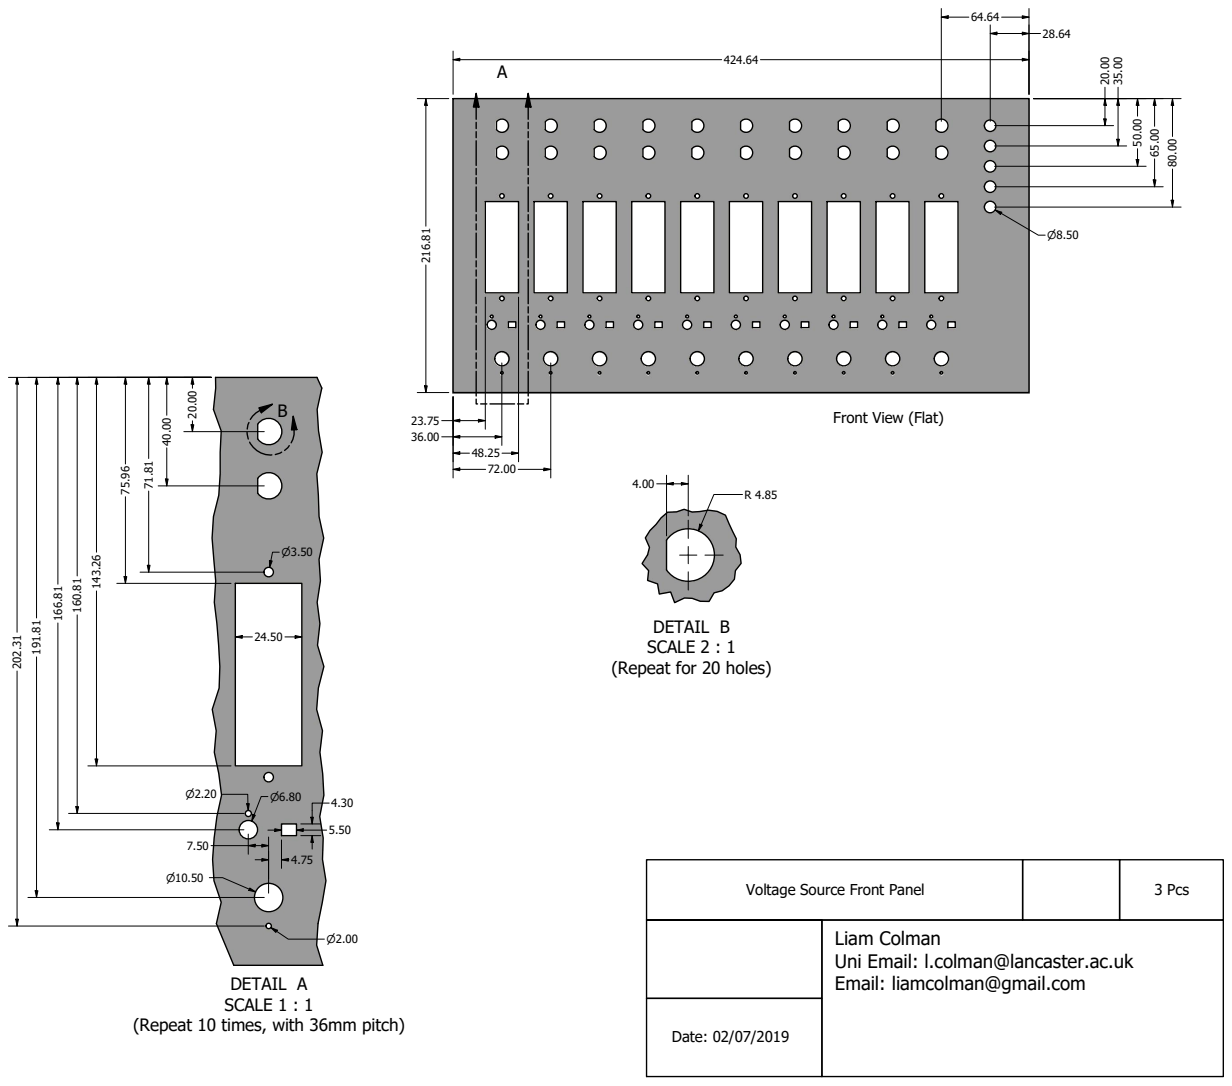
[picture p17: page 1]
DETAIL A SCALE 1 : 1; Date: 02/07/2019

Front View (Flat)

DETAIL B
SCALE 2 : 1
(Repeat for 20 holes)

Voltage Source Front Panel | | 3 Pcs

Liam Colman Uni Email: l.colman@lancaster.ac.uk Email: liamcolman@gmail.com

(Repeat 10 times, with 36mm pitch)

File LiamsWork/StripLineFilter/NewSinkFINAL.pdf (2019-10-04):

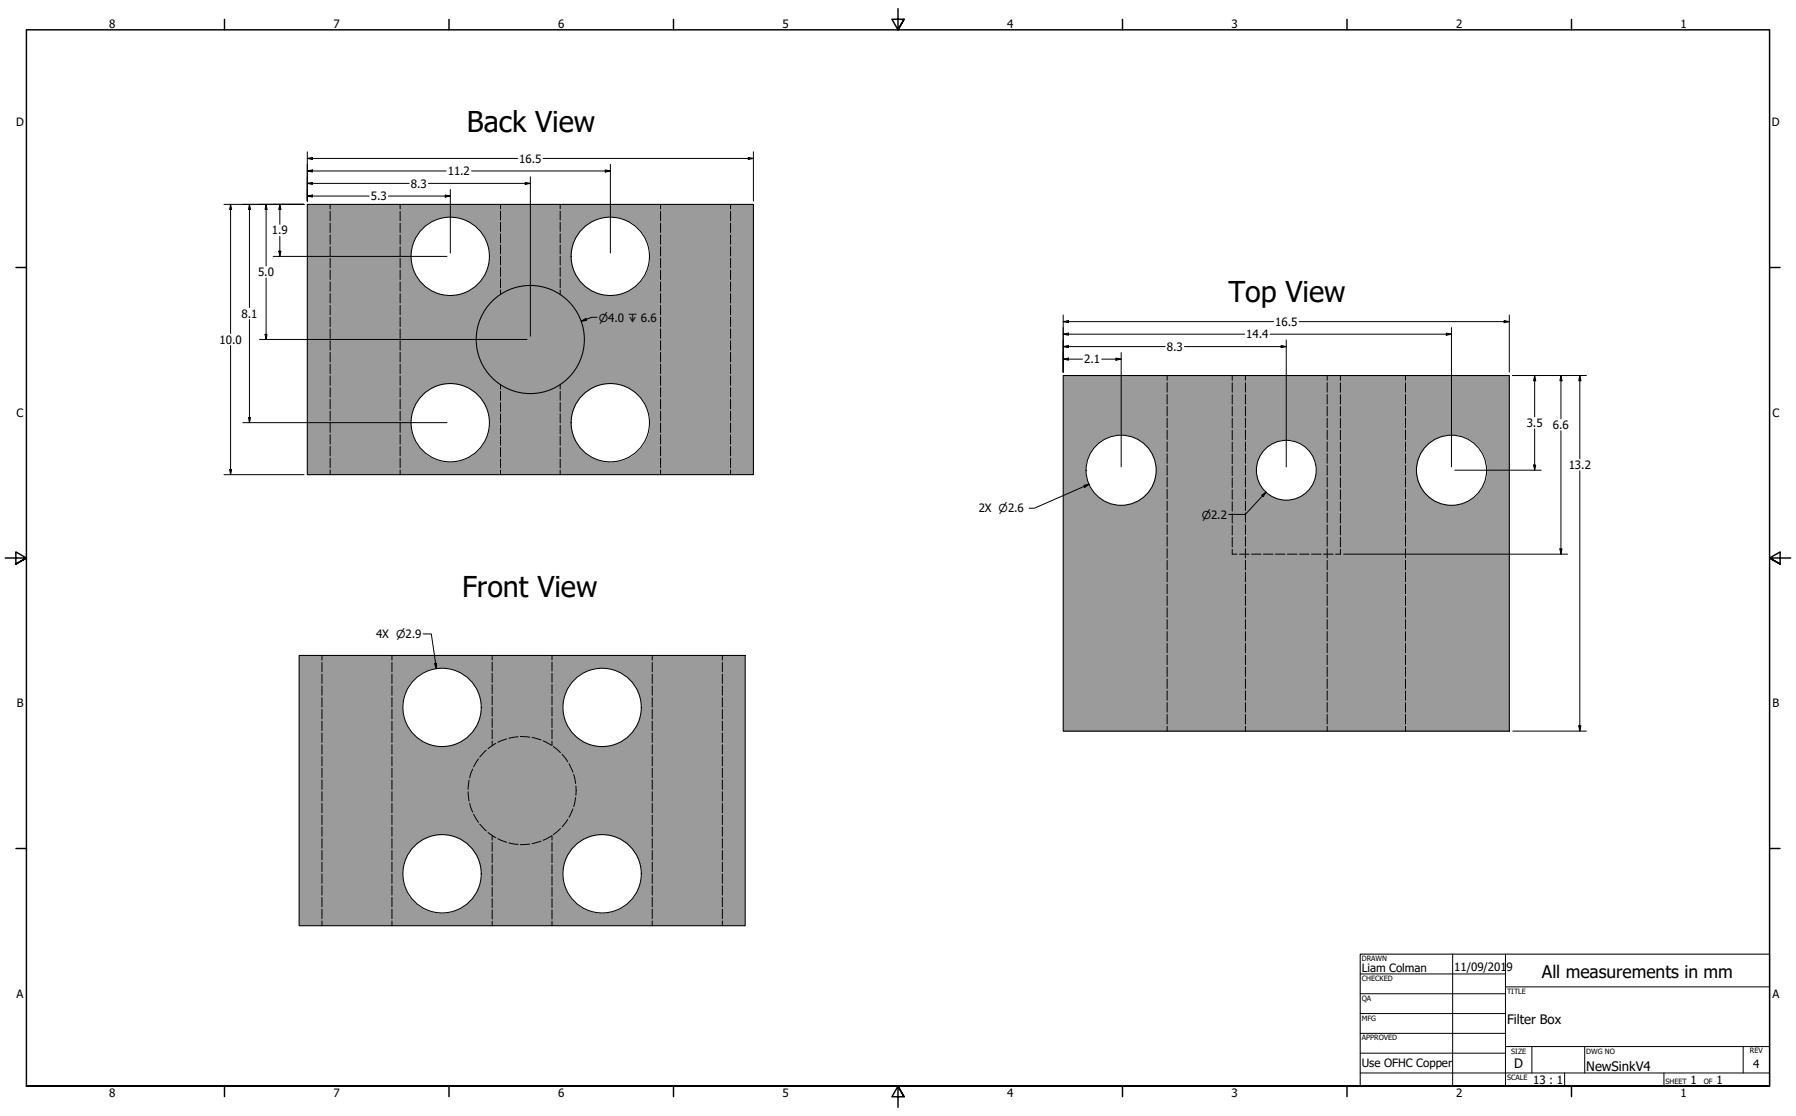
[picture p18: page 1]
Filter Box; Back View; Front View; Top View

DRAWN Liam Colman | 11/09/2019 | All measurements in mm

CHECKED

MFG

APPROVED

SIZE D | DWG NO NewSinkV4 | REV 4

Use OFHC Copper

SCALE 13 : 1 | SHEET 1 OF 1

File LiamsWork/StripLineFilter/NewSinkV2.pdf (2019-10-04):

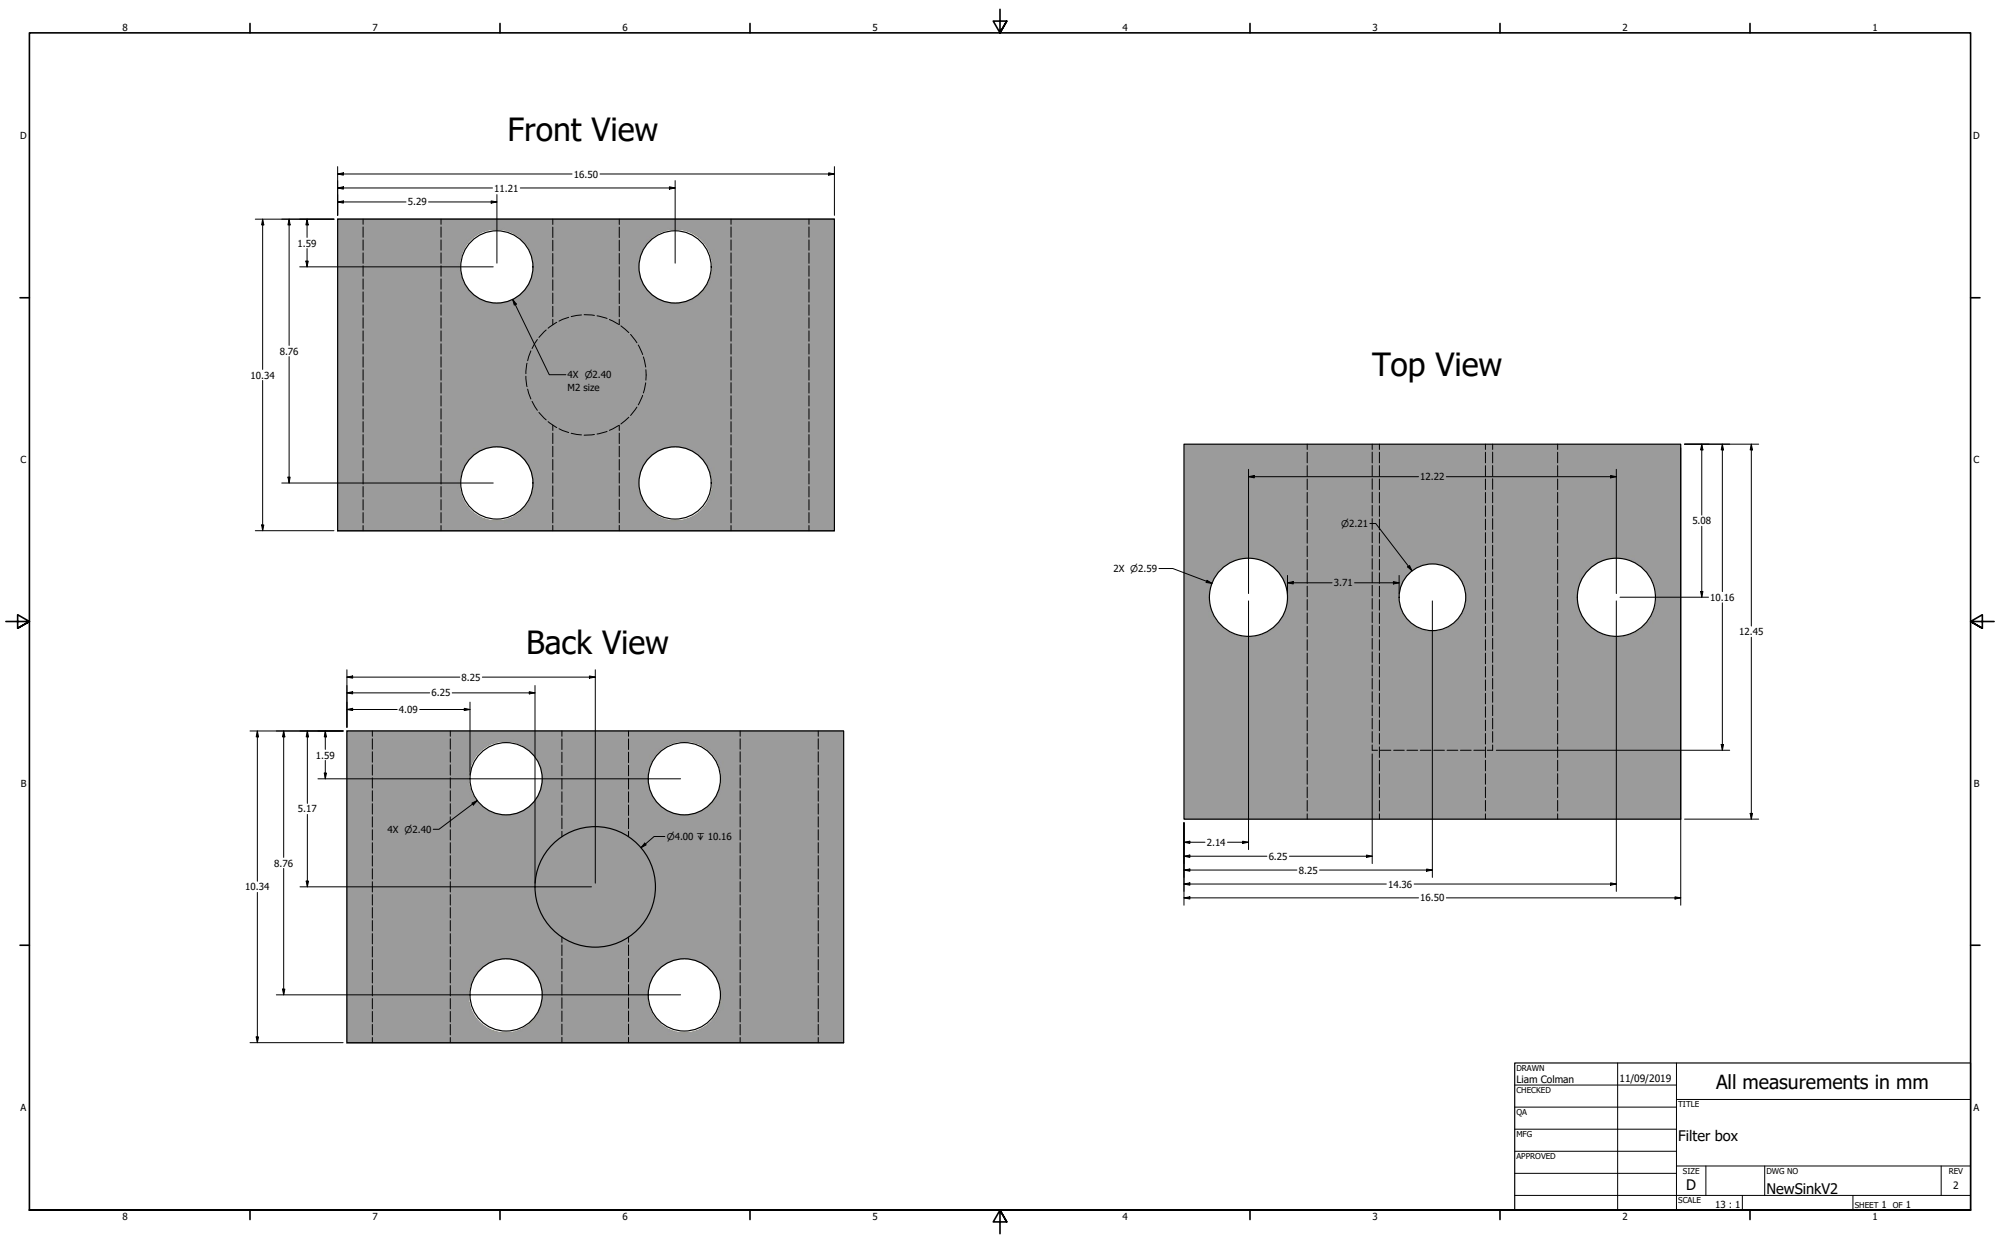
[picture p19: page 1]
Filter box; Front View; Back View; Top View; M2 size

DRAWN Liam Colman | 11/09/2019 | All measurements in mm

CHECKED

MFG

APPROVED

SIZE D | DWG NO NewSinkV2 | REV 2

SCALE 13 : 1 | | SHEET 1 OF 1

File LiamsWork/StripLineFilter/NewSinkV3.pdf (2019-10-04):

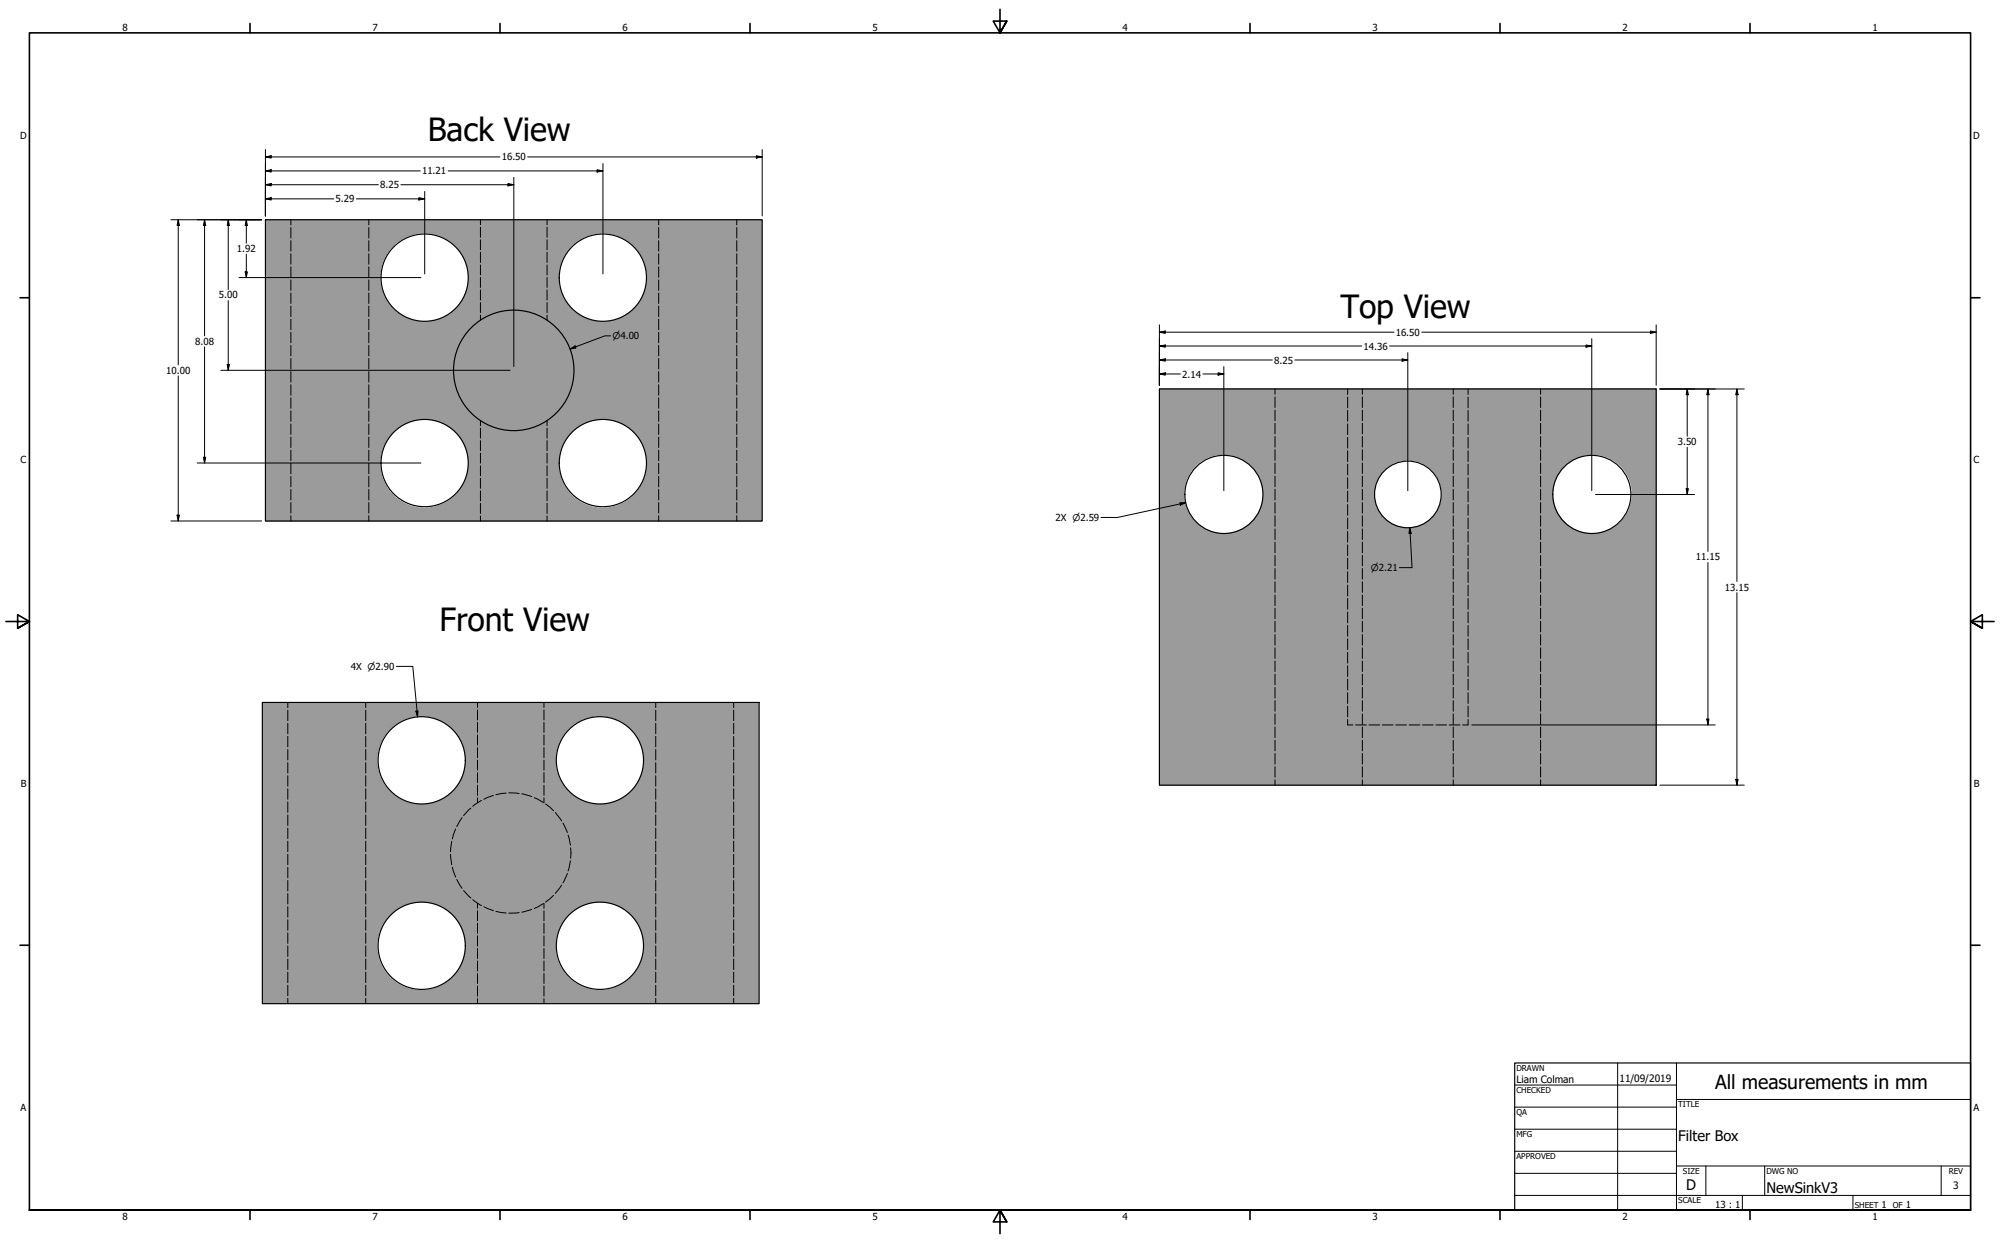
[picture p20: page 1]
Filter Box; Back View; Front View; Top View

DRAWN Liam Colman | 11/09/2019 | All measurements in mm

CHECKED

MFG

APPROVED

SIZE D | DWG NO NewSinkV3 | REV 3

SCALE 13 : 1 | | SHEET 1 OF 1

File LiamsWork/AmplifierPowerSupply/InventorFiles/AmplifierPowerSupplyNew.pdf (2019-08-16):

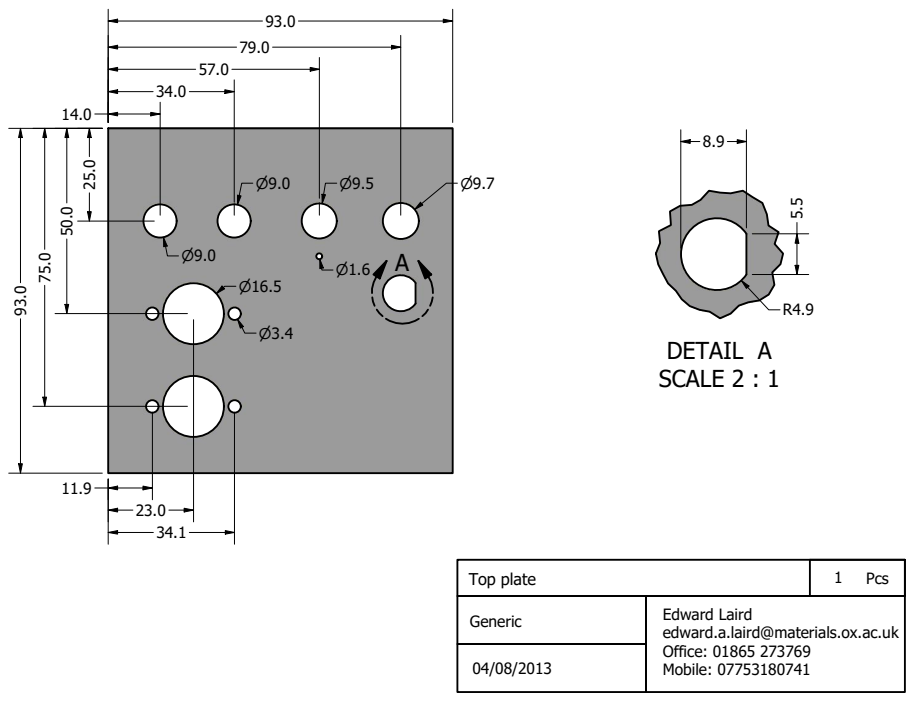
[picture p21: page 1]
DETAIL A SCALE 2 : 1

Top plate | 1 Pcs

Generic | Edward Laird edward.a.laird@materials.ox.ac.uk Office: 01865 273769 Mobile: 07753180741

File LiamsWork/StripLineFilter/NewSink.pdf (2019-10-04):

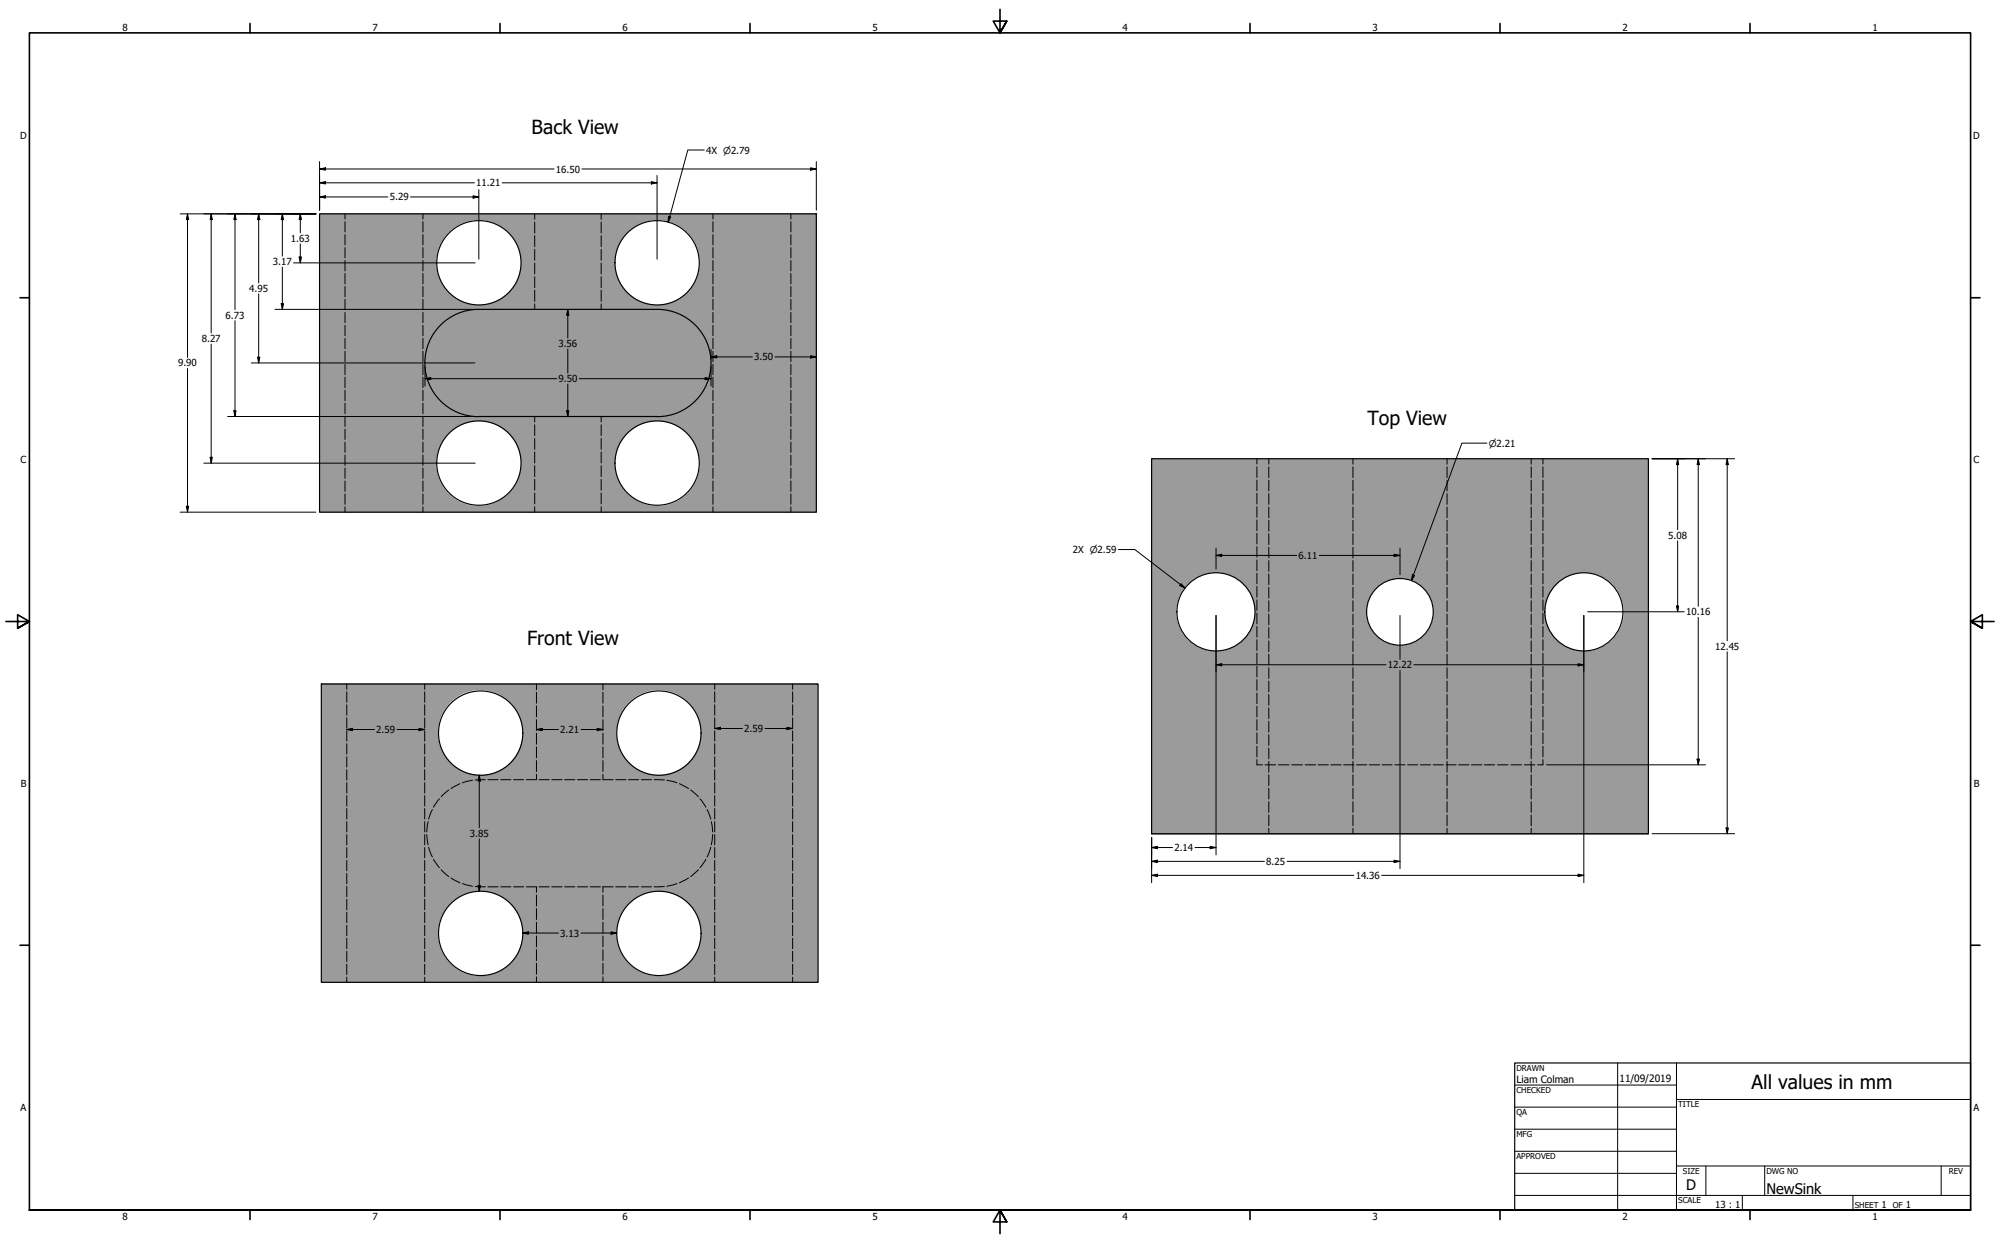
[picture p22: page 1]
Back View; Front View; Top View

DRAWN Liam Colman | 11/09/2019 | All values in mm

CHECKED

MFG

APPROVED

SIZE D | DWG NO NewSink | REV

SCALE 13 : 1 | | SHEET 1 OF 1

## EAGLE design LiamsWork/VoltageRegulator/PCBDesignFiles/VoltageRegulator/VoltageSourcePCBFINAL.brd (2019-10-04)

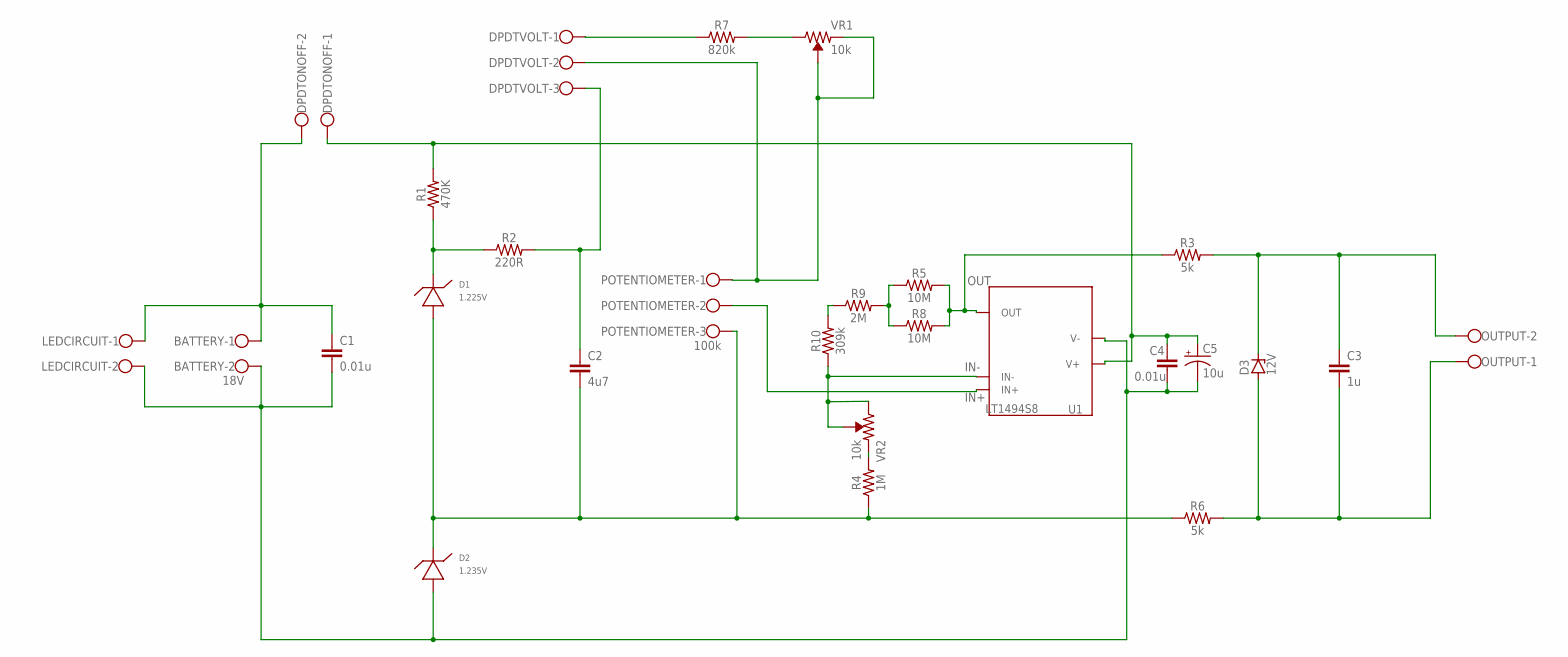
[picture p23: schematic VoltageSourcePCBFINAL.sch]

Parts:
BATTERY: 18V; W237-102
C1, C4: 0.01u; 0805
C2: 4u7; 0805
C3: 1u; 0805
C5: 10u; EIA7343
D1: 1.225V; S8PACKAGE
D2: 1.235V; SOIC-8PACKAGE
D3: 12V; SOT23
DPDTONOFF: W237-102
DPDTVOLT: W237-103
LEDCIRCUIT: W237-102
OUTPUT: W237-102
POTENTIOMETER: 100k; W237-103
R1: 470K; 0805
R2: 220R; 0805
R3, R6: 5k; 0805
R4: 1M; 0805
R5, R8: 10M; 0805
R7: 820k; 0805
R9: 2M; 0805
R10: 309k; 0805
U1: LT1494S8; S8PACKAGE
VR1, VR2: 10k; TRIMPOT-SMD-TC33X

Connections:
IN+: POTENTIOMETER.2, U1.3 (IN+)
IN-: R10.1, U1.2 (IN-), VR2.1 (CW), VR2.2 (WIPER)
unnamed: BATTERY.1, C1.1, DPDTONOFF.2, LEDCIRCUIT.1
unnamed: D1.6 (CATHODE), D1.8 (CATHODE), R1.1, R2.1
unnamed: C2.2, D1.4 (ANODE), D2.8 (CATHODE), POTENTIOMETER.3, R4.1, R6.1
unnamed: C2.1, DPDTVOLT.3, R2.2
unnamed: DPDTVOLT.2, POTENTIOMETER.1, VR1.2 (WIPER), VR1.3 (CCW)
unnamed: DPDTVOLT.1, R7.1
unnamed: R5.1, R8.1, R9.2
unnamed: C3.1, D3.3 (C), OUTPUT.2, R3.2
unnamed: C3.2, D3.1 (A), OUTPUT.1, R6.2
unnamed: R4.2, VR2.3 (CCW)
unnamed: R7.2, VR1.1 (CW)
unnamed: R9.1, R10.2
OUT: R3.1, R5.2, R8.2, U1.6 (OUT)
V+: C4.1, C5.A (+), DPDTONOFF.1, R1.2, U1.7 (V+)
V-: BATTERY.2, C1.2, C4.2, C5.C (-), D2.4 (ANODE), LEDCIRCUIT.2, U1.4 (V-)

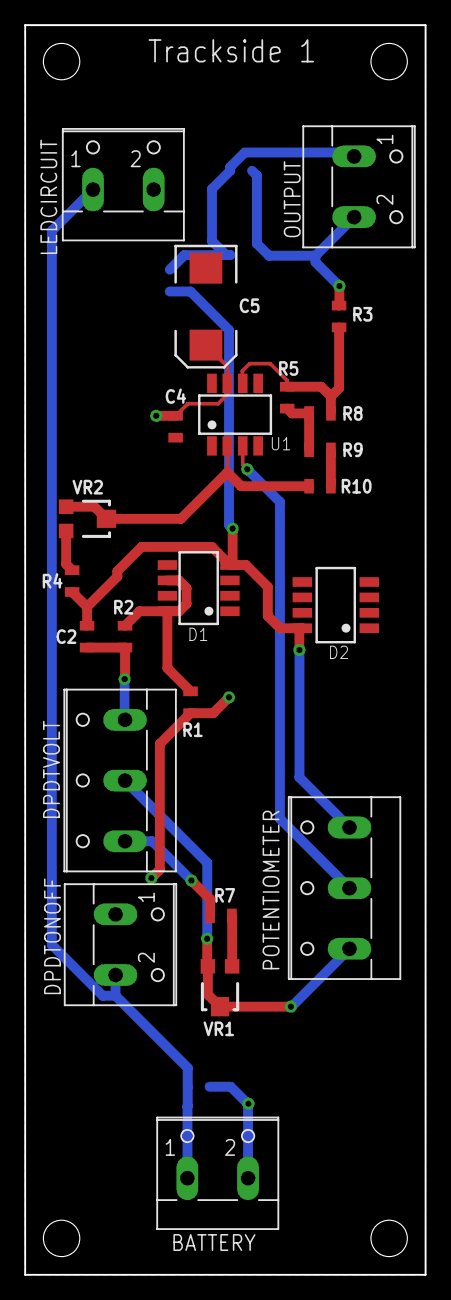
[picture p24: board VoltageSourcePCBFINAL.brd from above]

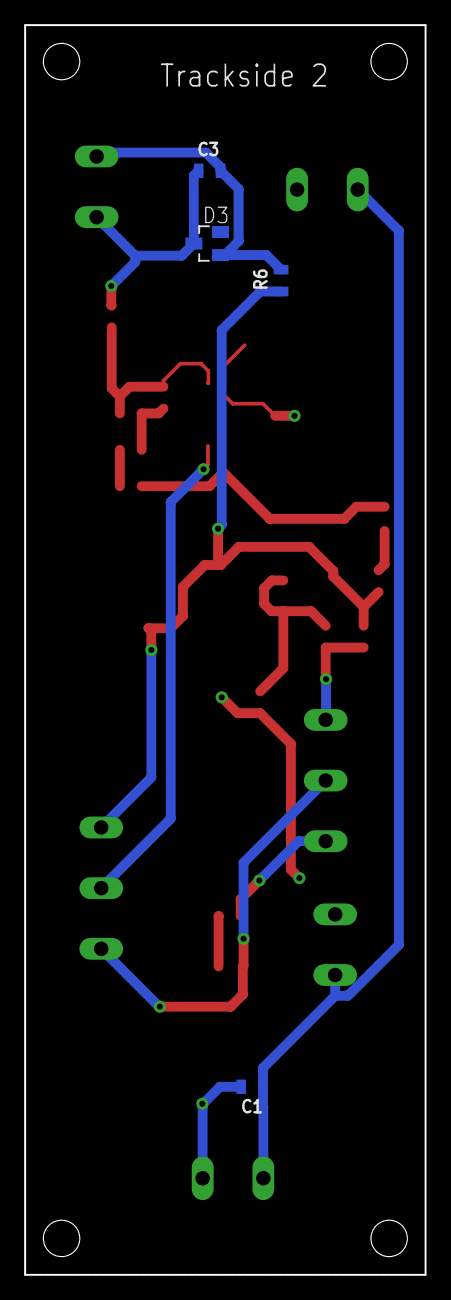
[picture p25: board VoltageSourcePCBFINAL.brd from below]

Board: 2 copper layers, 33.0 x 103.0 mm, 27 parts (4 on the bottom side), 17 nets.

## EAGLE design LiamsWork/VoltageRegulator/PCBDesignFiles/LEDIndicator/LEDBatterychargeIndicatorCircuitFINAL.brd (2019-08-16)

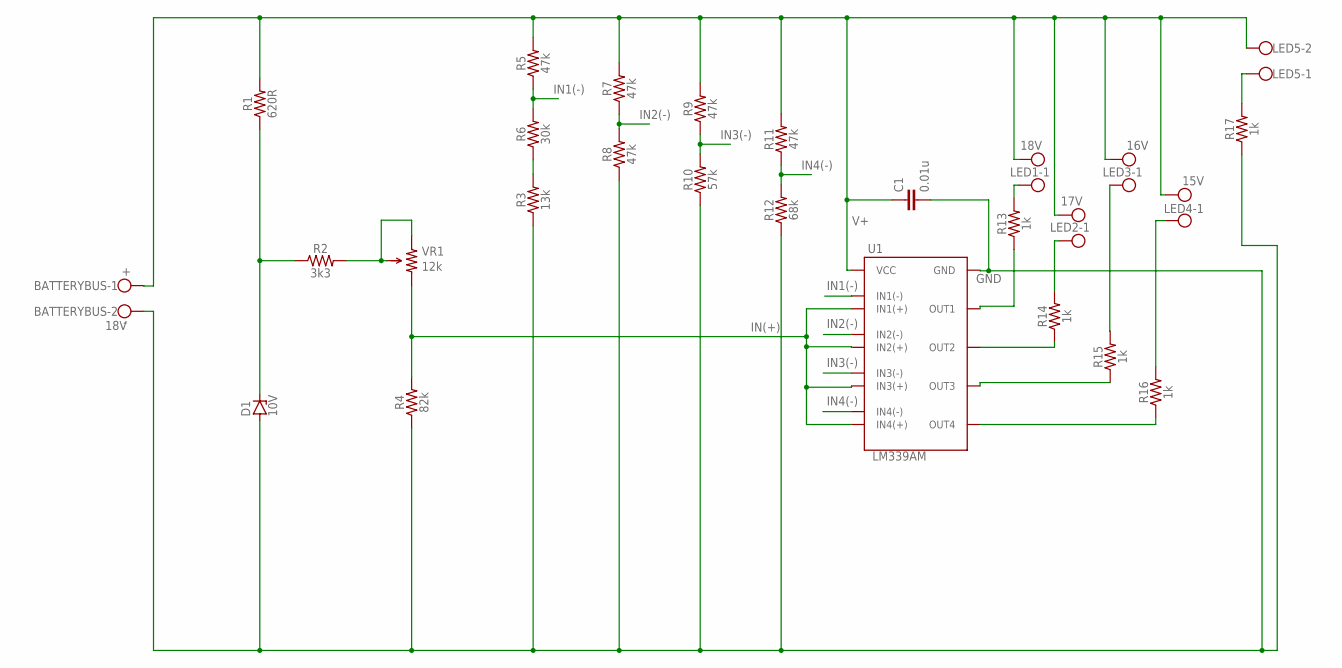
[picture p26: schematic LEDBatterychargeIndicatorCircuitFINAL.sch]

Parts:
BATTERYBUS: 18V; W237-102
C1: 0.01u; 0805
D1: 10V; SOT23
LED1: 18V; W237-102
LED2: 17V; W237-102
LED3: 16V; W237-102
LED4: 15V; W237-102
LED5: W237-102
R1: 620R; 0805
R2: 3k3; 0805
R3: 13k; 0805
R4: 82k; 0805
R5, R7, R8, R9, R11: 47k; 0805
R6: 30k; 0805
R10: 57k; 0805
R12: 68k; 0805
R13, R14, R15, R16, R17: 1k; 0805
U1: LM339AM
VR1: 12k; TRIMPOT3266W

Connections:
GND: BATTERYBUS.2, C1.2, D1.1 (A), R3.1, R4.1, R8.1, R10.1, R12.1, R17.1, U1.12 (GND)
IN1(-): R5.1, R6.2, U1.4 (IN1(-))
IN2(-): R7.1, R8.2, U1.6 (IN2(-))
IN3(-): R9.1, R10.2, U1.8 (IN3(-))
IN4(-): R11.1, R12.2, U1.10 (IN4(-))
IN(+): R4.2, U1.5 (IN1(+)), U1.7 (IN2(+)), U1.9 (IN3(+)), U1.11 (IN4(+)), VR1.1
unnamed: LED5.1, R17.2
unnamed: LED1.1, R13.2
unnamed: R13.1, U1.2 (OUT1)
unnamed: D1.3 (C), R1.1, R2.1
unnamed: R14.1, U1.1 (OUT2)
unnamed: R2.2, VR1.2 (WIPER), VR1.3
unnamed: LED2.1, R14.2
unnamed: LED3.1, R15.2
unnamed: R15.1, U1.14 (OUT3)
unnamed: R16.1, U1.13 (OUT4)
unnamed: LED4.1, R16.2
unnamed: R3.2, R6.1
V+: BATTERYBUS.1, C1.1, LED1.2, LED2.2, LED3.2, LED4.2, LED5.2, R1.2, R5.2, R7.2, R9.2, R11.2, U1.3 (VCC)

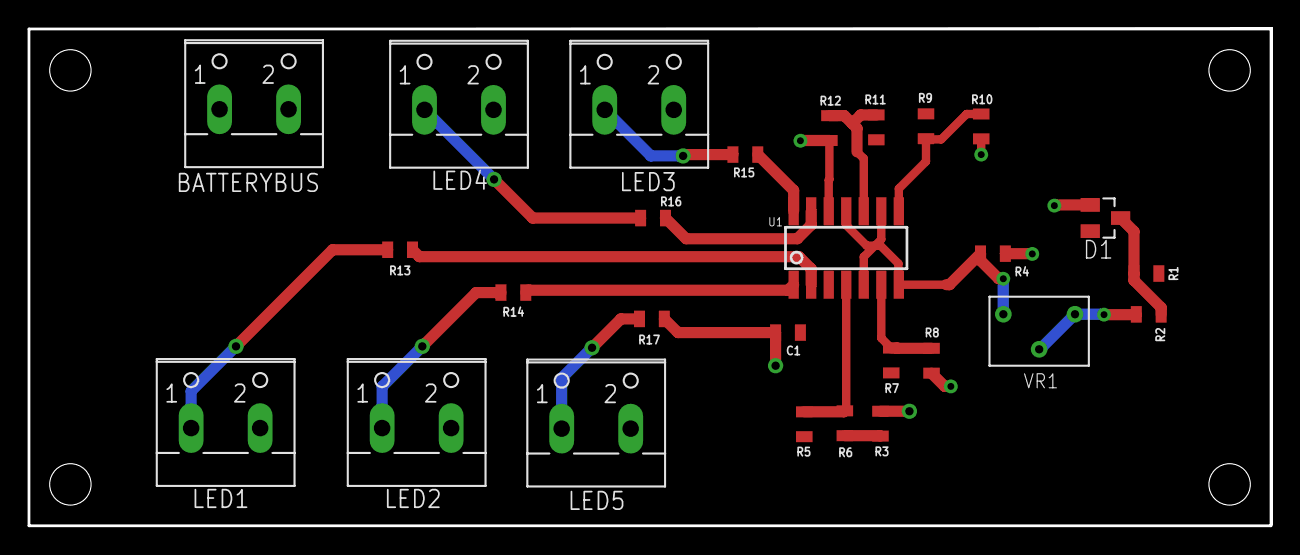
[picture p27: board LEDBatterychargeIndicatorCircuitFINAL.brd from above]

Board: 2 copper layers, 90.1 x 36.1 mm, 27 parts (0 on the bottom side), 19 nets.

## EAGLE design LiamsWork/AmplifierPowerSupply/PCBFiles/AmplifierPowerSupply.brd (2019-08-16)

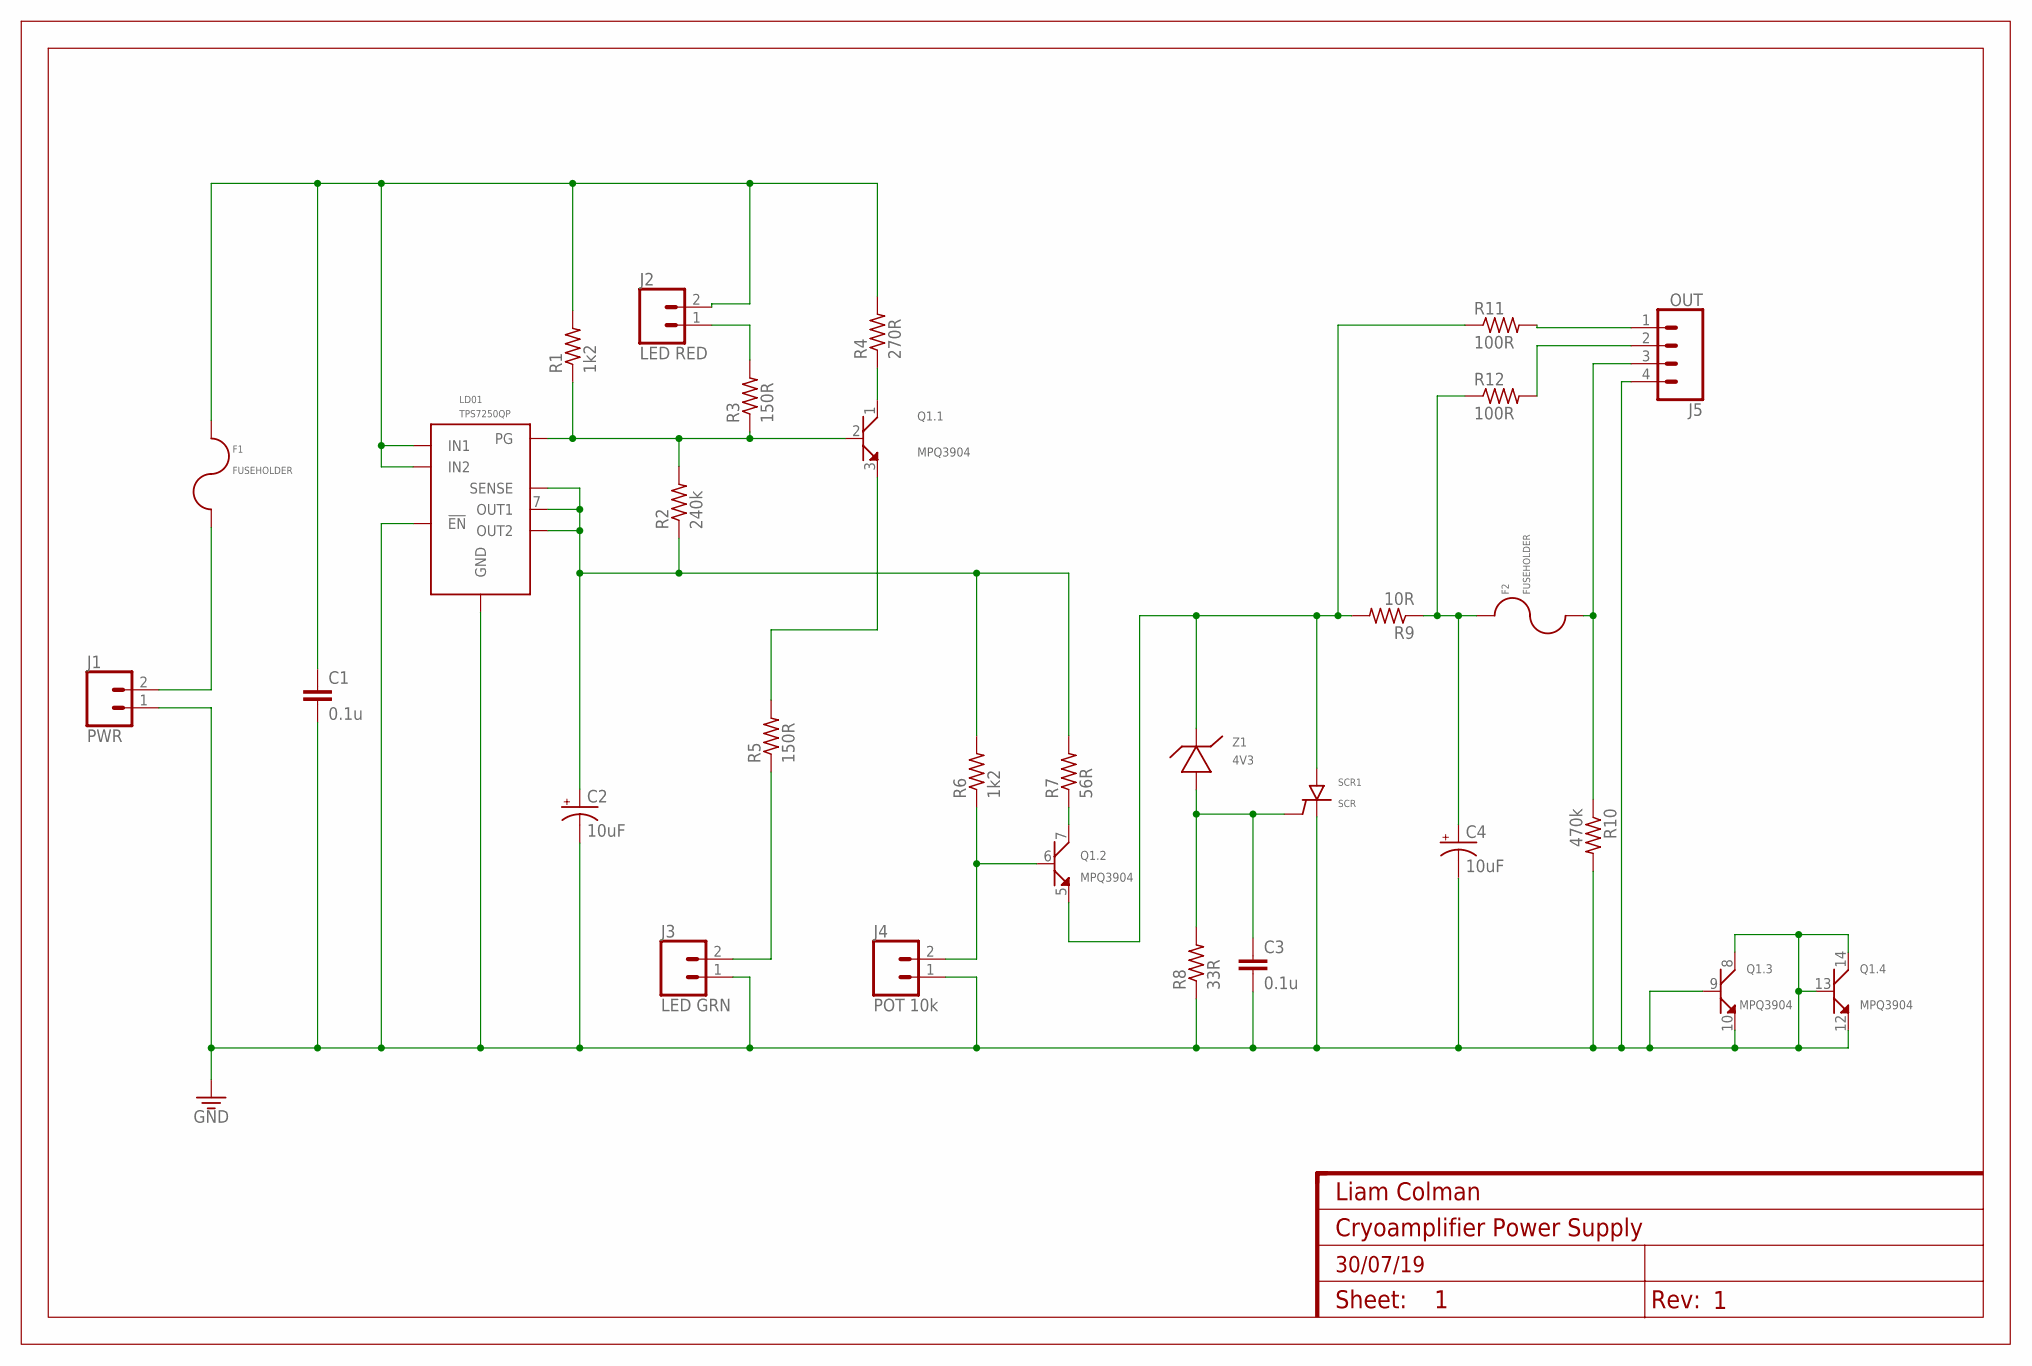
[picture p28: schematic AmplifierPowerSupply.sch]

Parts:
C1, C3: 0.1u; C1206K
C2, C4: 10uF; EIA3216
F1, F2: FUSEHOLDER
FRAME1: FRAMELIAM-A4; DUMMY
J1: PWR; 1X02
J2: LED RED; 1X02
J3: LED GRN; 1X02
J4: POT 10k; 1X02
J5: OUT; 1X04
LD01: TPS7250QP
Q1: MPQ3904
R1, R6: 1k2; R0805
R2: 240k; R0805
R3, R5: 150R; R0805
R4: 270R; R0805
R7: 56R; R0805
R8: 33R; R0805
R9: 10R; R0805
R10: 470k; R0805
R11, R12: 100R; R0805
SCR1: SCR; TO-92
Z1: 4V3; DZ2W04300L

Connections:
GND: C1.2, C2.-, C3.2, C4.-, J1.1, J3.1, J4.1, J5.4, LD01.3 (GND), LD01.4 (!EN!), Q1.8 (COLLECTOR), Q1.9 (BASE), Q1.10 (EMITTER), Q1.12 (EMITTER), Q1.13 (BASE), Q1.14 (COLLECTOR), R8.1, R10.2, SCR1.K (CATHODE)
unnamed: F1.P$2, J1.2
unnamed: C1.1, F1.P$1, J2.2, LD01.5 (IN1), LD01.6 (IN2), R1.2, R4.2
unnamed: J2.1, R3.2
unnamed: LD01.2 (PG), Q1.2 (BASE), R1.1, R2.2, R3.1
unnamed: J5.1, R11.2
unnamed: J5.2, R12.2
unnamed: C4.+, F2.P$1, R9.1, R12.1
unnamed: F2.P$2, J5.3, R10.1
unnamed: J4.2, Q1.6 (BASE), R6.1
unnamed: Q1.1 (COLLECTOR), R4.1
unnamed: Q1.3 (EMITTER), R5.2
unnamed: J3.2, R5.1
unnamed: Q1.7 (COLLECTOR), R7.1
unnamed: Q1.5 (EMITTER), R9.2, R11.1, SCR1.A (ANODE), Z1.1 (CATHODE)
unnamed: C2.+, LD01.1 (SENSE), LD01.7 (OUT1), LD01.8 (OUT2), R2.1, R6.2, R7.2
unnamed: C3.1, R8.2, SCR1.G (GATE), Z1.2 (ANODE)

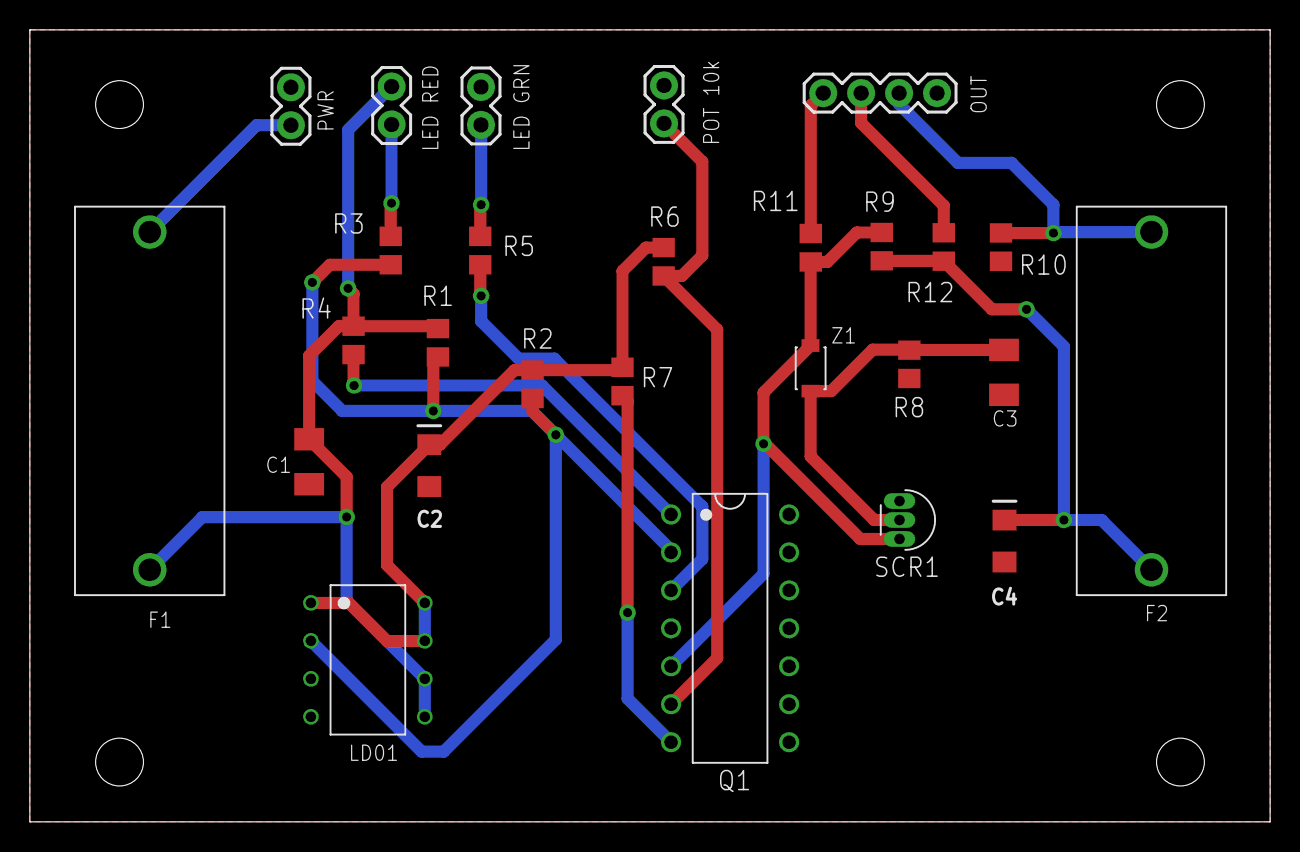
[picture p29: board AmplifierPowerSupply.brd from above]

Board: 2 copper layers, 83.0 x 53.0 mm, 28 parts (0 on the bottom side), 17 nets.

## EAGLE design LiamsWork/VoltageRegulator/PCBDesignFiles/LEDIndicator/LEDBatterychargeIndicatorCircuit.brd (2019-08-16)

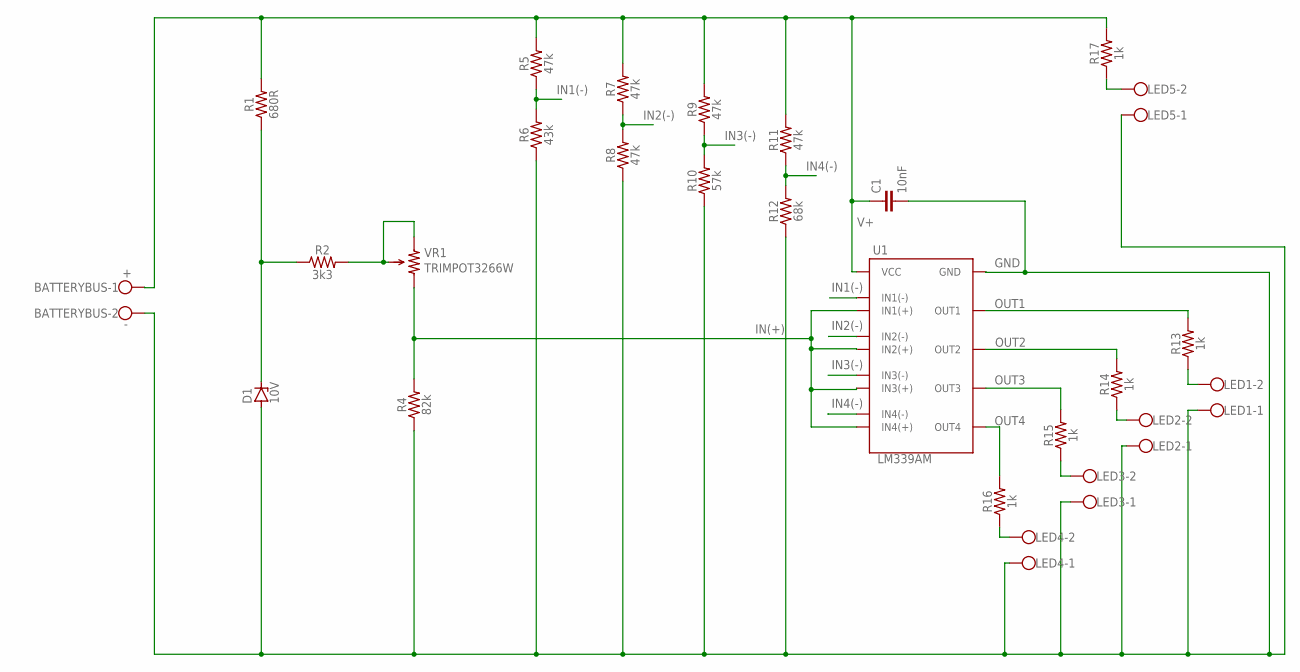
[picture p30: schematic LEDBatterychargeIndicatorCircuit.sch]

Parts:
BATTERYBUS: W237-102
C1: 10nF; C7.5B5
D1: 10V; F126Z12
LED1, LED2, LED3, LED4, LED5: W237-102
R1: 680R; 0805
R2: 3k3; 0805
R4: 82k; 0805
R5, R7, R8, R9, R11: 47k; 0805
R6: 43k; 0805
R10: 57k; 0805
R12: 68k; 0805
R13, R14, R15, R16, R17: 1k; 0805
U1: LM339AM
VR1: TRIMPOT3266W

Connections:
GND: BATTERYBUS.2, C1.2, D1.A, LED1.1, LED2.1, LED3.1, LED4.1, LED5.1, R4.1, R6.1, R8.1, R10.1, R12.1, U1.12 (GND)
IN1(-): R5.1, R6.2, U1.4 (IN1(-))
IN2(-): R7.1, R8.2, U1.6 (IN2(-))
IN3(-): R9.1, R10.2, U1.8 (IN3(-))
IN4(-): R11.1, R12.2, U1.10 (IN4(-))
IN(+): R4.2, U1.5 (IN1(+)), U1.7 (IN2(+)), U1.9 (IN3(+)), U1.11 (IN4(+)), VR1.1
unnamed: D1.C, R1.1, R2.1
unnamed: R2.2, VR1.2 (WIPER), VR1.3
unnamed: LED1.2, R13.1
unnamed: LED2.2, R14.1
unnamed: LED3.2, R15.1
unnamed: LED4.2, R16.1
unnamed: LED5.2, R17.1
OUT1: R13.2, U1.2 (OUT1)
OUT2: R14.2, U1.1 (OUT2)
OUT3: R15.2, U1.14 (OUT3)
OUT4: R16.2, U1.13 (OUT4)
V+: BATTERYBUS.1, C1.1, R1.2, R5.2, R7.2, R9.2, R11.2, R17.2, U1.3 (VCC)

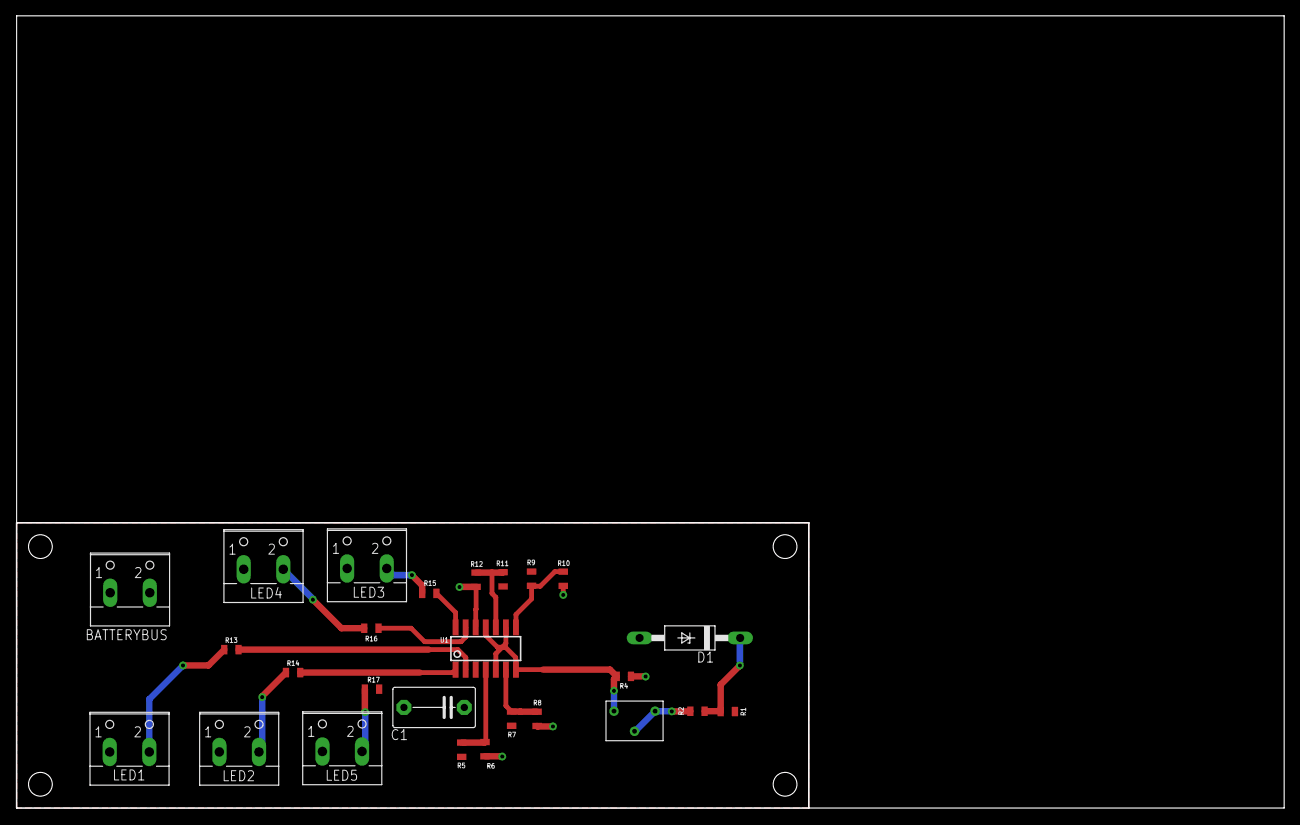
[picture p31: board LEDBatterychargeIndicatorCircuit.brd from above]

Board: 2 copper layers, 160.0 x 100.0 mm, 26 parts (0 on the bottom side), 18 nets.

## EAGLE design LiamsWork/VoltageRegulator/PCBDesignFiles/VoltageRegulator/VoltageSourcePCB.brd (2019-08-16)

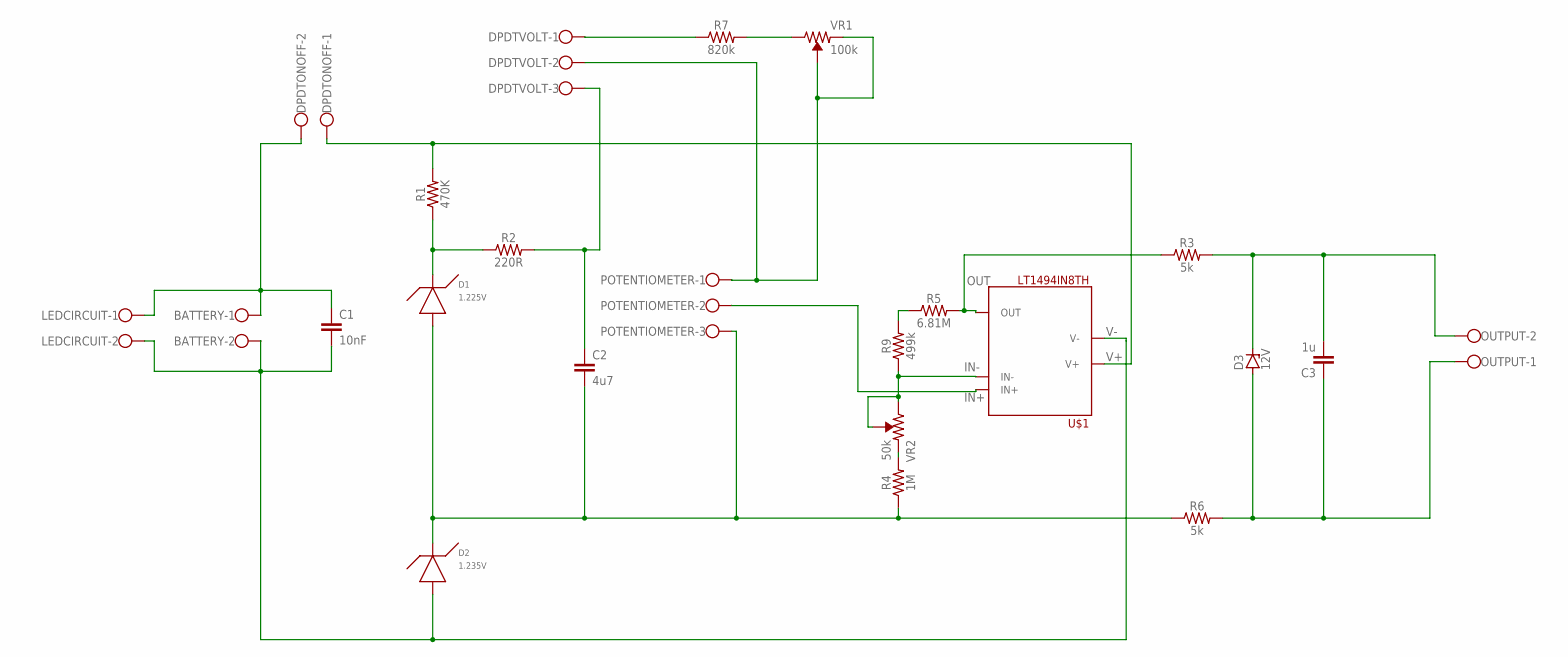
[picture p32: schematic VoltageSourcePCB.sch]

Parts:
BATTERY: W237-102
C1: 10nF; C5B2.5
C2: 4u7; C22.5B11
C3: 1u; C150-072X183
D1: 1.225V; LT1004CZ
D2: 1.235V; LT1004CZ
D3: 12V; C1702-15
DPDTONOFF: W237-102
DPDTVOLT: W237-103
LEDCIRCUIT: W237-102
OUTPUT: W237-102
POTENTIOMETER: W237-103
R1: 470K; 0805
R2: 220R; 0805
R3, R6: 5k; 0805
R4: 1M; 0805
R5: 6.81M; 0805
R7: 820k; 0805
R9: 499k; 0805
U$1: LT1494IN8TH; LT1494TH
VR1: 100k; TRIMPOT-SMD-TC33X
VR2: 50k; TRIMPOT-SMD-TC33X

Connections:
IN+: POTENTIOMETER.2, U$1.3 (IN+)
IN-: R9.1, U$1.2 (IN-), VR2.1 (CW), VR2.2 (WIPER)
unnamed: D1.CATHODE, R1.1, R2.1
unnamed: C2.2, D1.ANODE, D2.CATHODE, POTENTIOMETER.3, R4.1, R6.1
unnamed: C2.1, DPDTVOLT.3, R2.2
unnamed: DPDTVOLT.2, POTENTIOMETER.1, VR1.2 (WIPER), VR1.3 (CCW)
unnamed: DPDTVOLT.1, R7.1
unnamed: BATTERY.1, C1.1, DPDTONOFF.2, LEDCIRCUIT.1
unnamed: C3.2, D3.C, OUTPUT.2, R3.2
unnamed: C3.1, D3.A, OUTPUT.1, R6.2
unnamed: R4.2, VR2.3 (CCW)
unnamed: R7.2, VR1.1 (CW)
unnamed: R5.1, R9.2
OUT: R3.1, R5.2, U$1.6 (OUT)
V+: DPDTONOFF.1, R1.2, U$1.7 (V+)
V-: BATTERY.2, C1.2, D2.ANODE, LEDCIRCUIT.2, U$1.4 (V-)

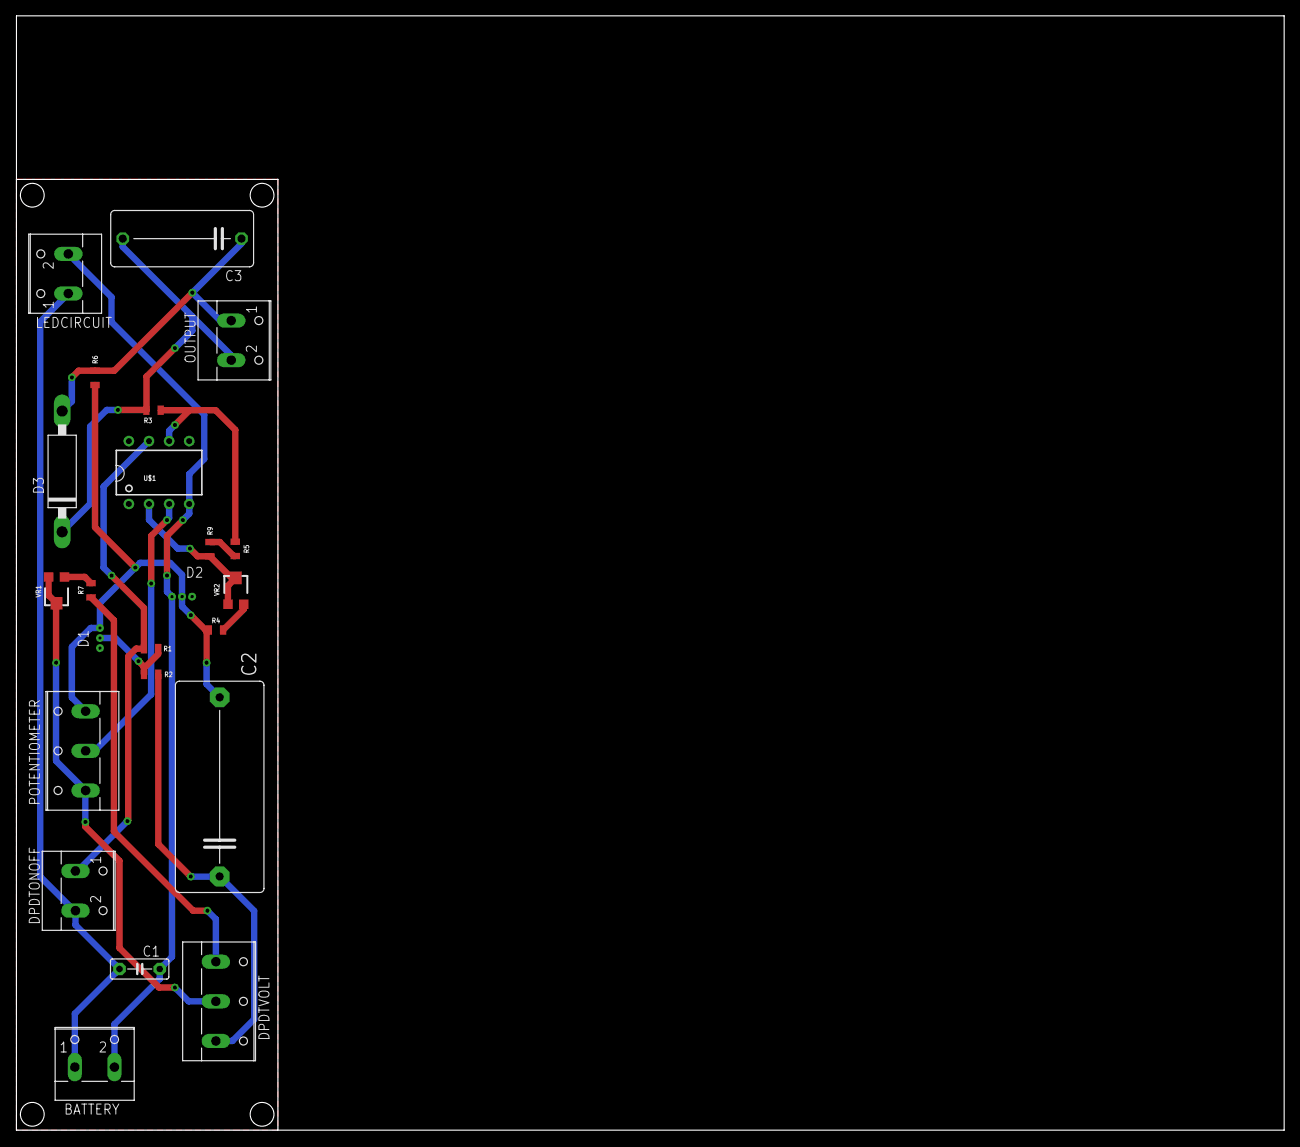
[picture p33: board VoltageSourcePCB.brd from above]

Board: 2 copper layers, 160.0 x 140.6 mm, 23 parts (0 on the bottom side), 16 nets.

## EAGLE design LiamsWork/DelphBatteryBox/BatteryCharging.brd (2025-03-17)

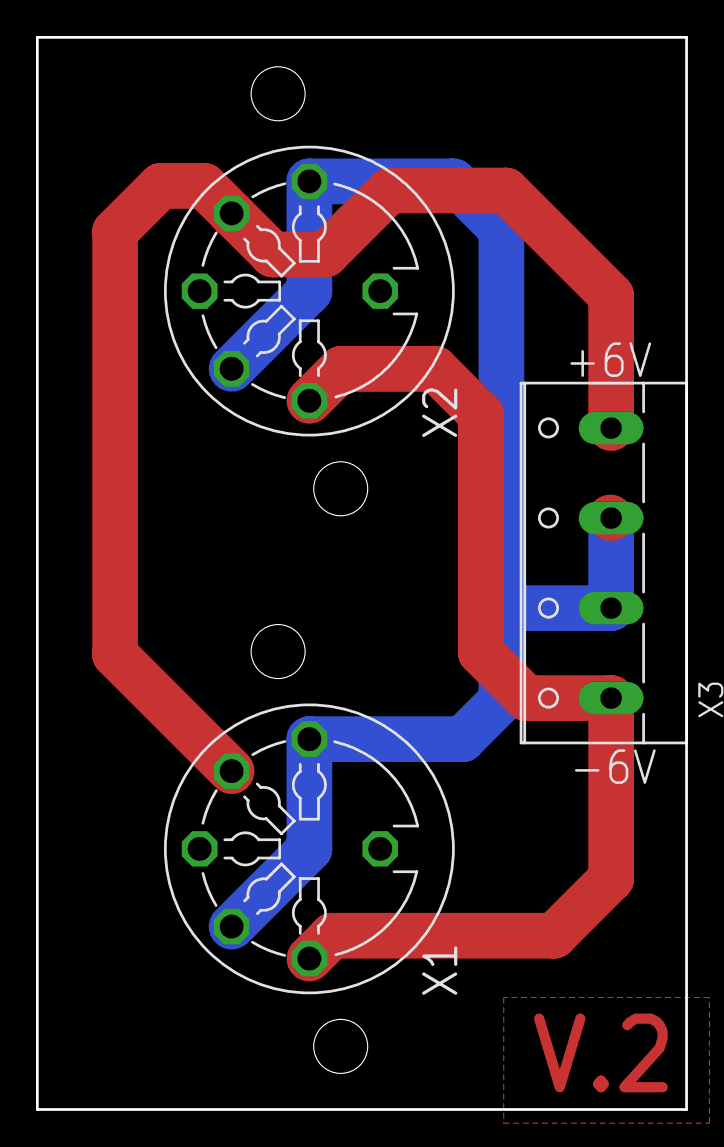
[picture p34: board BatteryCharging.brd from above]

Board: 2 copper layers, 36.1 x 59.6 mm, 3 parts (0 on the bottom side), 4 nets.

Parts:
X1, X2: MAB5SV
X3: W237-4

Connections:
0V: X1.3, X1.4, X2.3, X2.4, X3.2, X3.3
+6V: X1.5, X2.5, X3.4
-6V: X1.1, X2.1, X3.1
GND: X1.2, X1.PE, X2.2, X2.PE

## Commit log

2019-06-24 Add Liam folder
    [BatteryCharging.brd, BatteryCharging.sch]
2019-06-25 Added additional screw terminal
2019-06-27 Updated Battery PCB files
    [BatteryCharging.brd]
2019-06-28 Updated PCB design & Gerber files
    [BatteryCharging.brd]
2019-07-10 Changed name of repository and added voltage source files
    [BatteryCharging.brd, BatteryCharging.sch, LEDBatterychargeIndicatorCircuit.sch, VoltageSourcePCB.sch]
2019-07-10 Altered file path for Voltage Source files and Battery box files
    [BatteryCharging.brd, BatteryCharging.sch, LEDBatterychargeIndicatorCircuit.sch, VoltageSourcePCB.sch]
2019-08-16 Files updated to contain recent developments, added Amplifier power supply file
    [AmplifierPowerSupply.brd, AmplifierPowerSupply.sch, AmplifierPowerSupplyNew.dwg, AmplifierPowerSupplyNew.ipt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]
2019-10-04 Added updated files for all of the things I've done at the end of the internship
    [1534309620.xlsx, BOM.xlsx, BatteryCharging.brd, LEDBatterychargeIndicatorCircuit.sch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]
2025-03-17 connect 0V between both batteries
2025-03-17 version number on board
    [BatteryCharging.brd]
2025-03-17 adjust connector mounting holes
    [BatteryCharging.brd]

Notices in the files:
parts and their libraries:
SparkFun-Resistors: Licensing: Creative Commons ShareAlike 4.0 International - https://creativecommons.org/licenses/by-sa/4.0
